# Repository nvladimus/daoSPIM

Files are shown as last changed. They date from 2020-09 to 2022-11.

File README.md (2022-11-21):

# daoSPIM




**D**ual-view **a**daptive **o**ptics **s**elected **p**lane **i**llumination **m**icroscope makes multiview light-sheet microscopy compatible with microfluidic devices, by correcting optical aberrations with a deformable mirror (DM). Its unique optical design allows correcting aberrations in two arms with a single DM simultaneously.
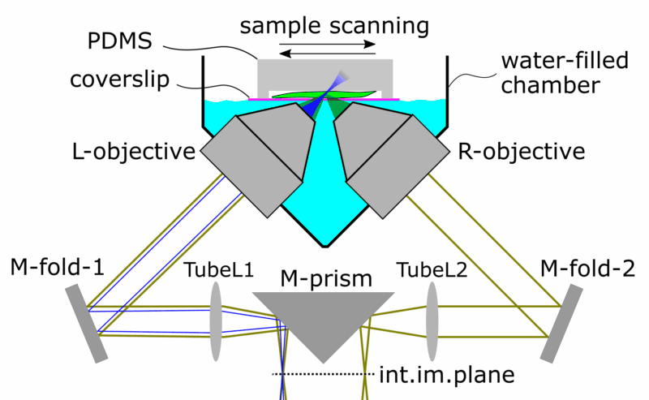
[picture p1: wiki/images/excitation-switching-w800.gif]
Optical layout: chamber


## Hardware overview
The [Wiki](https://github.com/nvladimus/daoSPIM/wiki/overview) page provides a high-level system overview. 

The [/wiki](./wiki) folder contains implementation details:
* [BOM](./wiki/BOM.xlsx)
* [CAD](./wiki/custom_parts_cad) files for custom-made mechanical parts
* [PCB](./wiki/arm_switcher) design files for arm switcher board

## Microscope control software
The microscope is controlled via [GUI program](./microscope_control) which links together:
- camera (Hamamatsu Orca Flash4.3)
- stage (ASI MS-2000)
- light-sheet generator (based on NI PCIe-6321 DAQ board and arm switcher)
- deformable mirror (ImagineOptics Mirao52e)
- electro-tunable lens (Optotune EL-16-40-TC-VIS-5D-C)

DM is optimized in a separate Jupyter [notebook](./dm_optimization/) using a fluorescent bead image. The resulting DM command can be loaded in the GUI  [program](./microscope_control) and used thereafter.

## Citation
If you use any code or materials from this repo in your work, please cite our work as

**Dual-view light-sheet imaging through tilted glass interface using a deformable mirror** \
Nikita Vladimirov, Friedrich Preusser, Jan Wisniewski, Ziv Yaniv, Ravi Anand Desai, Andrew Woehler, Stephan Preibisch. [Biomedical Optics Express, 2021](https://doi.org/10.1364/BOE.416737).

To cite the code specifically, please use the following DOI:



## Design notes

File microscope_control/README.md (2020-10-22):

## daoSPIM control
The software provides GUI for microscope control:
- advanced camera control (input and output triggers, acq. modes), 
- light sheet generation via galvo scanning (NI DAQmx task configuration)
- stage scanning (with TTL pulses at defined spatial intervals)
- deformable mirror control (loading and applying commands from file)
- electrotunable lens control (manual offsetting the ETL power)
- streaming images into HDF5 file (Fiji/BigDataViewer flavor) at high speed (currently up to 60Hz)




## Hardware requirements
 - PC with Windows 7/10, x64.
 - camera Hamamatsu Orca Flash4.3.
 - NI DAQmx PCIe board with at least 2 AO channels for galvo and laser modulation (e.g. PCIe-6321).
 - XY stage from ASI (MS-2000 controller).
 - ETL Optotune EL-16-40-TC-VIS-5D-C.
 - deformable mirror ImagineOptics Mirao52e.

### Installation 
(optional) Create and activate local environment from the command line, to keep things tidy
```
C:\Users\user\daoSPIM> cd microscope_control
C:\Users\user\daoSPIM> python -m venv venv
C:\Users\user\daoSPIM> venv\Scripts\activate.bat
(venv) C:\Users\user\daoSPIM>
```
Install dependencies 
```
pip install --upgrade pip
pip install -r requirements.txt
```
Launch the program
```
python dao_spim_control.py
```

### GUI overview
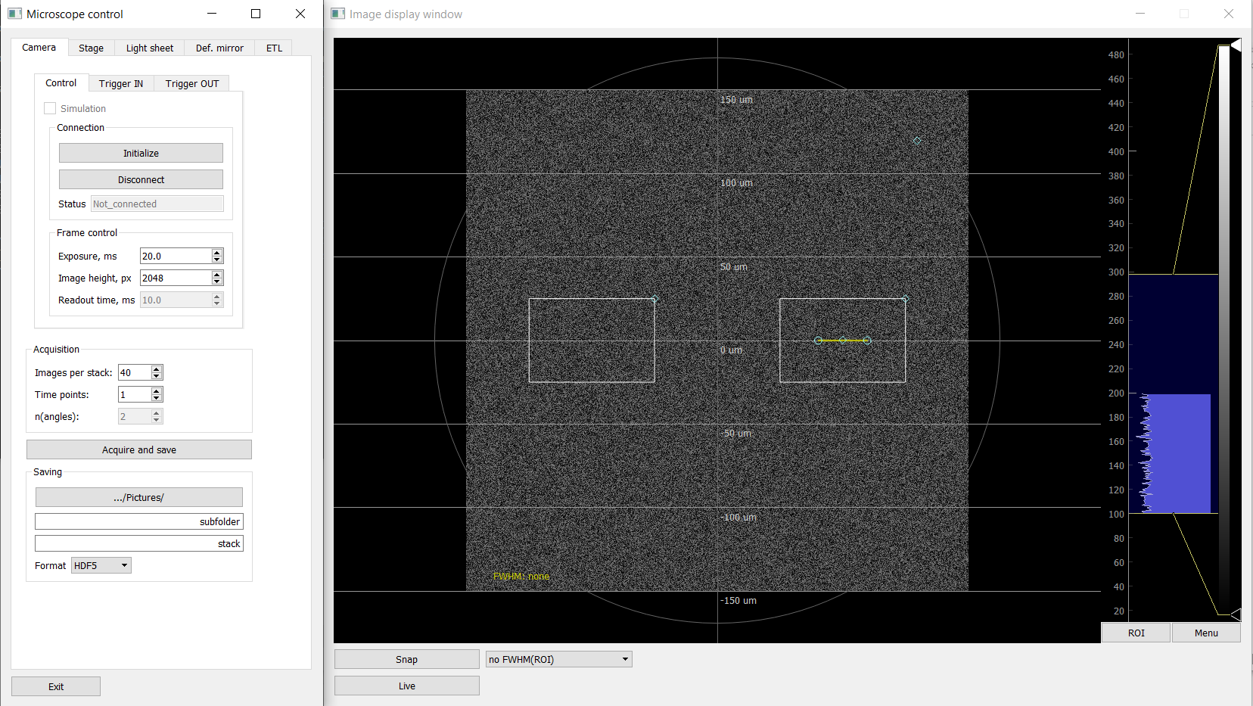
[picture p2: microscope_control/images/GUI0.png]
GUI


### Design principle
The code is still in development, but the author tried to keep it maximally modular and reusable. Each device is represented by a single file with GUI, controller and configuration code, independent from other devices. The main program file `dao_spim_control.py` connects these modules into a system. The GUI building is simplified by using a local library [widget.py](./src/widget.py) which takes care of PyQt5 low-level code.
See [device_template.py](./src/device_template.py) for example. 

The module files for these and other devices are independently available at [kekse](https://github.com/nvladimus/kekse) repo.

The camera control code was adapted from H.Babcock's [storm-control](https://github.com/ZhuangLab/storm-control/tree/master/storm_control/sc_hardware/hamamatsu) software.

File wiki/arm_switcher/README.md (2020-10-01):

# Arm switcher
This is a small Teensy-powered PCB that counts camera pulses and adds a user-defined voltage bias to the input signal after every *N* pulses. Designed to allow fast switching of light-sheet excitation laser (galvo) between left and right arms, to run in synch with camera. The software-based solution (eg in Python) would be too slow, hence this board.

PCB

## Inputs
* camera exposure pulses *Trig_in* (digital)
* galvo voltage *g_in* (analog) that makes a swipe motion for light sheet generation.

## Output
* analog signal *g_in + V0* (during first *N* camera pulses), *g_in + V1* (during next *N* pulses), then *g_in + V0* again, etc. 
* (for debugging) analog bias voltage alone: *V0* or *V1* .

## User-defined parameters:
   - camera pulse count *N* (>=1)
   - bias voltage *V0, V1* (-5 to +5 V)

## Setting parameters
Parameters are set via serial communication (baud rate 9600):
```
?ver #get the firmware version
n 10 #set switching period to 10 trigger pulses
?n #read the switching period
reset #reset the counter
v0 -0.45 #set voltage0 bias, [Volt]
v1 0.32 #set voltage1 bias, [Volt]
```

## Bill of materials
The PCB can be ordered from [Aisler](https://aisler.net/p/MTFTDGBD) (min. order 3 boards)

[Parts list](BOM.xlsx)

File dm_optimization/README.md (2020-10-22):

## Deformable mirror shape optimization 



### Software requirements
- Python 3.6, x64 (e.g. Anaconda)
- (optional) create and activate [local environment](/microscope_control#installation)
- Hamamatsu DCAM drivers
- Mirao52e dll drivers (x64)

### Hardware requirements
- PC with OS Windows 7/10
- camera Hamamatsu Orca4.3
- deformable mirror Mirao52e

### Sample requirements
- fluorescent bead resistant to bleaching,
- initial SNR is relatively high (ideally >10),
- only one fluorescent bead is present in the ROI, in both views,
- the bead is illuminated in wide-field or defocused light sheet mode. Using thin light sheet is discouraged to avoid light sheet walking off the bead (non-specific variation of the metric).

### Algorithm peculiarities
- the image metric is minimized;
- the gain grows in inverse proportion to the (decreasing) metric;
- the initial gain should be relatively small to avoid divergence (hopping on big bumps of the gradient);
- the algorithm tracks the position of a bead within the ROI and adjusts the ROI position if the bead drifts over time;
- the shape of DM is averaged between left and right halfs of the aperture, to add stability.

### Disclaimer
This notebook execution depends on particular hardware configuration and experimental conditions, and cannot be exactly reproduced. It was run several times after the original experiment in simulation mode to make the presentation more clear, so the cells are not numbered consecutively.

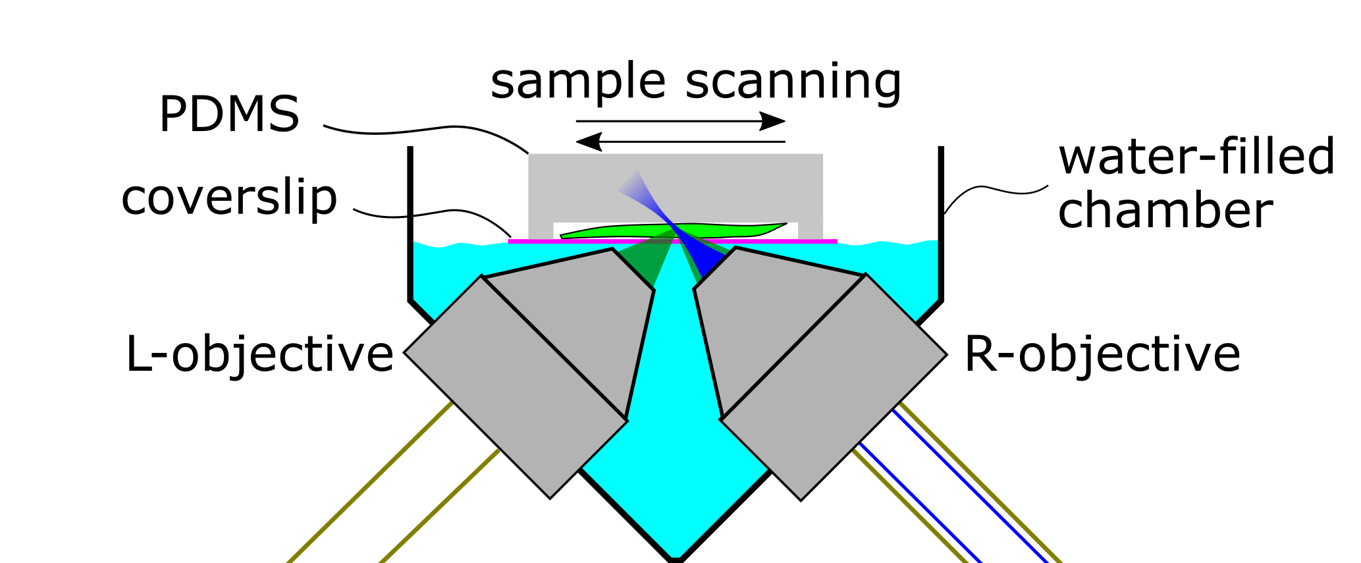
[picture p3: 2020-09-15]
wiki/images/ChamberOpticalLayout.png

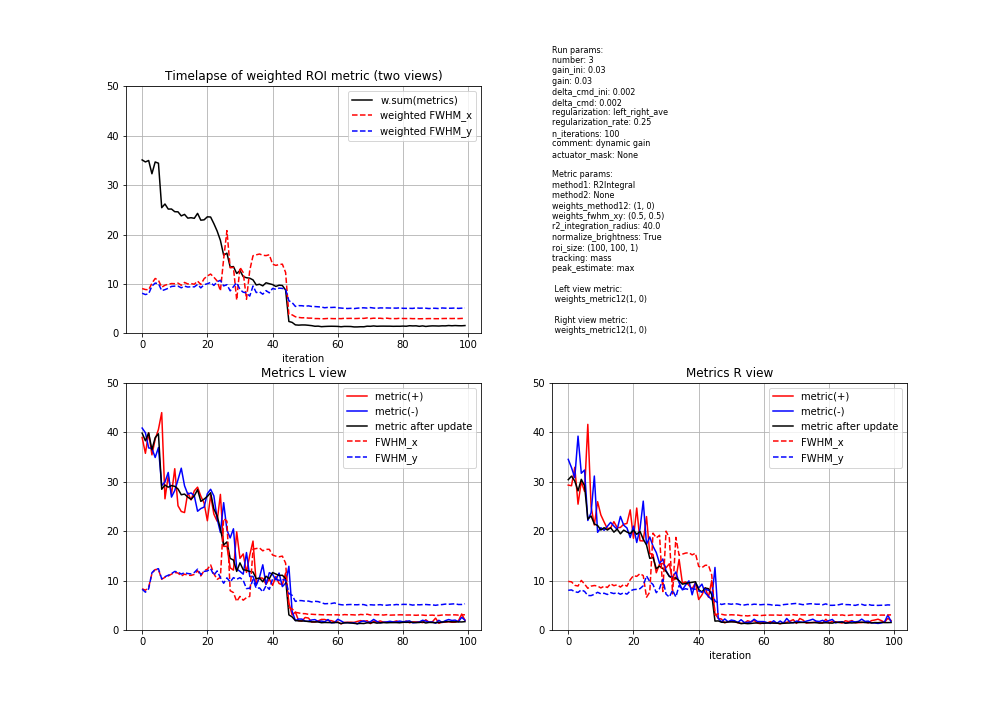
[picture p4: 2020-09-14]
dm_optimization/2020-02-18_optimization_examples/Run3_report.png

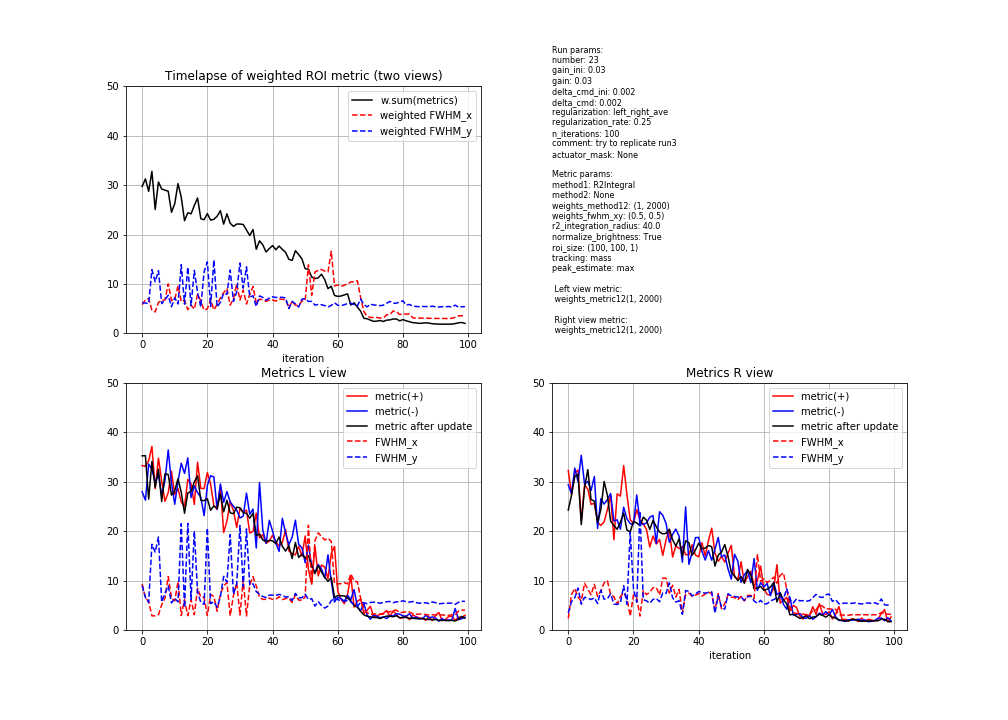
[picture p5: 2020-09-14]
dm_optimization/2020-02-18_optimization_examples/Run23_report.png

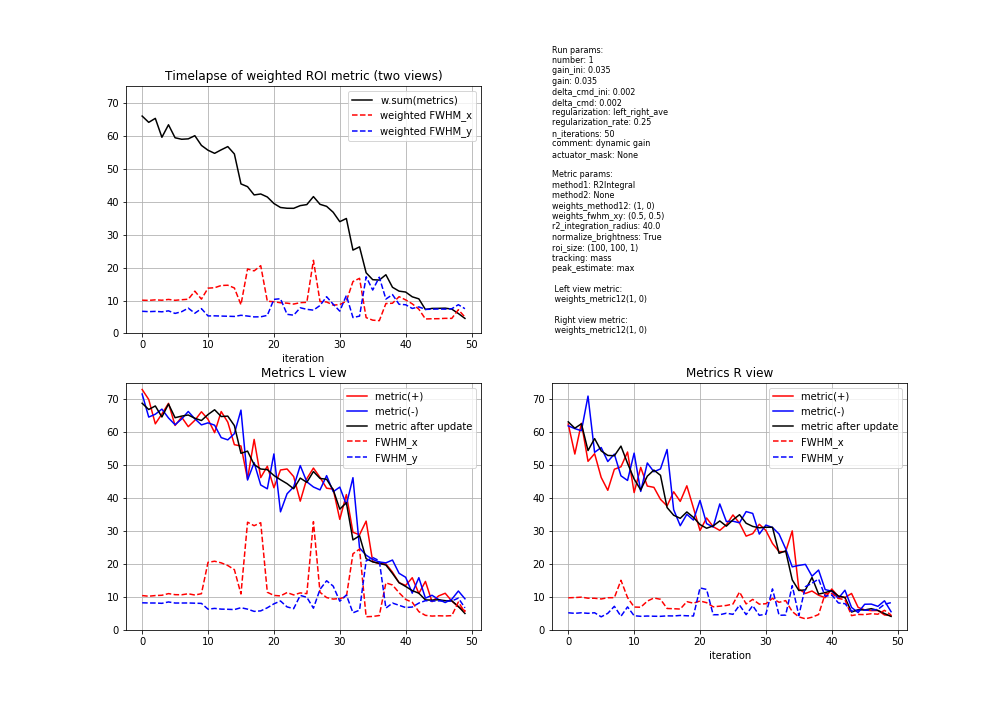
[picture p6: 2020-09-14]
dm_optimization/2020-02-18_optimization_examples/Run1_report.png

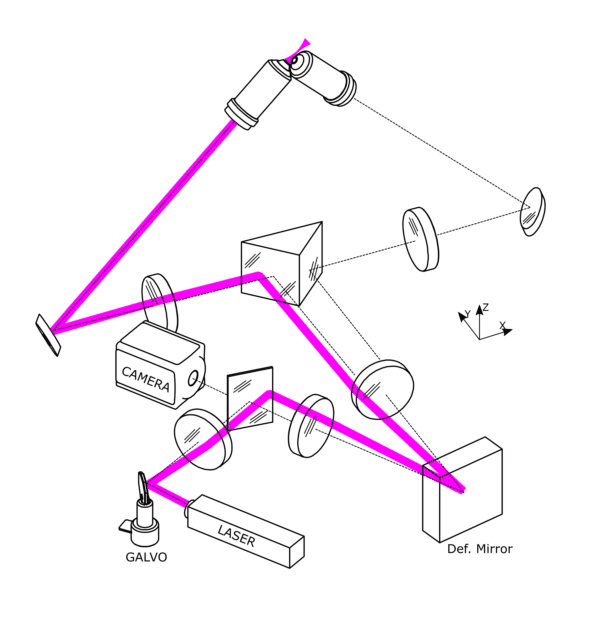
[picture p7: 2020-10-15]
wiki/images/excitation_switching3d_w600.gif

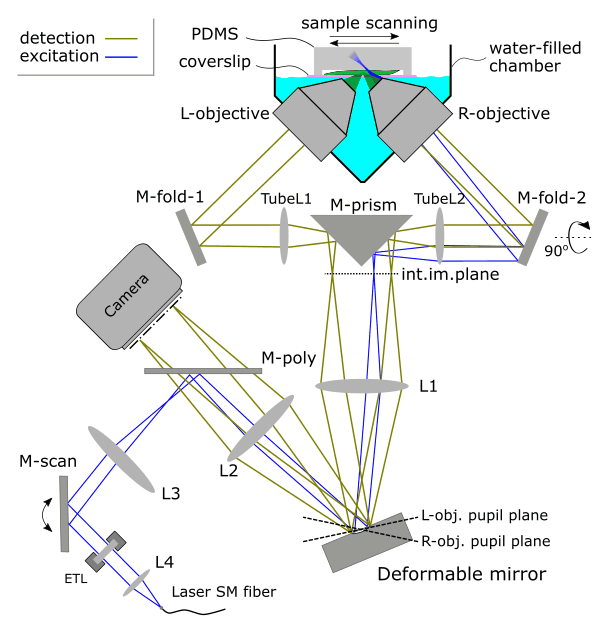
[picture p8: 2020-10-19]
wiki/images/excitation-switching.gif

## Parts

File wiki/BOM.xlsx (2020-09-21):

Component | Product | Manufacturer/Distributor | Price, EUR | Qty | Subtotal
Optomechanics
Objective | 40x/0.8 water-dipping apochromatic objective WD 3.5 mm, N40X-NIR. | Nikon / Thorlabs | 2850 | 2 | 5700
Objective mount | Z-Axis Translation Mount, 30 mm Cage Compatible, SM1Z. | Thorlabs | 187 | 2 | 374
Tube lens (TubeL1, TubeL2) | f=250mm mounted achromats, 25mm diam., AC254-250-A-ML | Thorlabs | 96 | 2 | 192
Prism mirror (M-prism) | Enhanced aluminium right angle mirror, legs 50 mm, #47-006 | Edmund Optics | 310 | 1 | 310
Prism mirror mount | Angle adjustment stage: Mini rotation stage 7R7E | Standa | 232 | 1 | 232
 | Connecting plate: 2CP7R7-273 | Standa | 90 | 1 | 90
 | XY adjustment: Low Profile Two-Axis Aluminium Translation Stage 7T273-10T | Standa | 384 | 1 | 384
Folding mirror (M-fold1, M-fold2) | Broadband Dielectric Elliptical Mirror, BBE1-E02 | Thorlabs | 92 | 2 | 184
Folding mirror mount | 45° Mount for 1" Elliptical Optics, H45E1 | Thorlabs | 114 | 2 | 228
 | Kinematic mount, KM100 | Thorlabs | 36 | 2 | 72
Relay lens L2 | f=400mm achromat, AC508-400-A-ML, 50.8 mm diam. | Thorlabs | 135 | 1 | 135
Relay lens L1 | f=450 mm achromat, diam. 40 mm, # 49-282 | Edmund Optics | 141 | 1 | 141
Deformable mirror, DM | Mirao52e | Imagine Optics | 21670 | 1 | 21670
Camera | Orca Flash 4v3 | Hamamatsu | 12500 | 1 | 12500
Detection cleanup filter | Quad-band filter ZET405/488/561/640mv2, 25.4mm Diam., mounted. | Chroma | 476 | 1 | 476
Laser | Skyra fiber-coupled, 405, 488, 561, 638 nm. MF-561-638-488-405-050-050-050-050-130 | Cobolt | 21765 | 1 | 21765
Fiber collimator assembly | Lens L4: f=10 mm mounted achromat, AC080-010-A-ML | Thorlabs | 67 | 1 | 67
 | Thread adapter: S1TM12 | Thorlabs | 22 | 1 | 22
 | Fiber coupler: FC/APC fiber adapter, SM1FCA | Thorlabs | 30 | 1 | 30
Electro-tunable lens assembly, ETL | ETL: EL-16-40-TC-VIS-5D-C, -3 to +2 diopter, 16 mm aperture. | Optotune | 780 | 1 | 780
 | Lens Driver 4i | Optotune | 280 | 1 | 280
 | Hirose 6-way cable | Optotune | 85 | 1 | 85
 | XY adjustment: XY translation stage, ST1XY-S/M. | Thorlabs | 364 | 1 | 364
 | Folding mirror: 1" Broadband Dielectric Elliptical Mirror, BBE1-E02. | Thorlabs | 92 | 1 | 92
 | Mirror mount: kinematic mirror mount KCB1EC/M | Thorlabs | 189 | 1 | 189
Scanning mirror, M-scan | Galvo mirror: 1D galvo system GVS001, silver-coated | Thorlabs | 937 | 1 | 937
 | Adapter: 30 mm Cage System Adapter GCM001 | Thorlabs | 135 | 1 | 135
Scan lens L3 | Mounted achromat f=125 mm, AC254-125-A-ML | Thorlabs | 96 | 1 | 96
Polychroic mirror, M-poly | ZT405/488/561/640rpcv2-UF2, 26 x 38 x 2mm, ID IN061199 | Chroma | 495 | 1 | 495
XY scanning motorized stage | Stage: 120x75mm travel, FTP flat-top stage with TE2000 bottom plate, 4TPI, scan-optimized X axis, without anti-backlash gear. Model MS-2000. #S562-2235B | ASI | 6950 | 1 | 6950
 | Controller: MS2000, with TTL pulse (ENC_INT) firmware. | ASI | 3600 | 1 | 3600
 | Stage Insert | custom-made | 0 | 1 | 0
Z-translation manual stage | ULTRAlign™ Precision stage, 12.7 mm travel, M-461-X-M | Newport | 526 | 1 | 526
 | Micrometer head, high-resolution, HR-13. | Newport | 128 | 1 | 128
Sample holder for 22x22 mm coverslip | Custom design, machined from stainless steel | Protolabs | 450 | 1 | 450
Optical table | T46H | Nexus/Thorlabs | 6301 | 1 | 6301
Computer hardware
Acquisition workstation | Precision Tower 7910, Windows 10 Professional | Dell | 6630 | 1 | 6630
DAQ | NI PCIe-6321 Multifunction I/O Device | National Instruments | 750 | 1 | 750
 | Connector block BNC 2110 | National Instruments | 450 | 1 | 450
 | BNC shielded cable SHC68-68-EPM | National Instruments | 167 | 1 | 167
Software
Microscope control | Custom-written, Python 3.6, PyQt5 | self | 0 | 1 | 0
Optical simulations | Zemax Optics Studio | Zemax | 4151 | 1 | 4151
CAD design | Autodesk Inventor, Education license | Autodesk | 0 | 1 | 0
 |  |  |  | Total | 98128

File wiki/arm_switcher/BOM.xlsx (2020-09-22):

Component | Model | Price, EUR | Qty | Subtotal
Arduino-compatible MCU | Teensy 2.0 | 28 | 1 | 28
DAC breakout board | MCP4725 | 3.5 | 1 | 3.5
opAmp | UA741 | 0.4 | 2 | 0.8
Voltage inverter | ICL7660 | 1.9 | 1 | 1.9
Power regulator 5V | L7805A | 0.46 | 1 | 0.46
BNC sockets | see detailed_bom.csv | 1 | 4 | 4
Barrel connector | see detailed_bom.csv | 0.5 | 1 | 0.5
Resistors, capacitors, trimpots | see detailed_bom.csv | 2 | 1 | 4
custom PCB | https://aisler.net/p/MTFTDGBD | 12 | 1 | 12
 |  |  | Total | 55.16

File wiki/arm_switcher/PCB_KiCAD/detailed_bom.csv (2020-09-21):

Reference | Value | Footprint | Datasheet | Category | DK_Datasheet_Link | DK_Detail_Page | Description | Digi-Key_PN | Family | MPN | Manufacturer | Status | Height | Manufacturer_Name | Manufacturer_Part_Number | Mouser Part Number | Mouser Price/Stock
U1 | Teensy2.0_(Arduino) | teensy_footprints:Teensy2.0
R1 | 10k | Resistor_THT:R_Axial_DIN0207_L6.3mm_D2.5mm_P10.16mm_Horizontal | ~
J1 | Trigger IN | my_components:BNC_female_jack_TE_1-1634505-0 | ~
J2 | Galvo signal IN | my_components:BNC_female_jack_TE_1-1634505-0 | ~
J3 | DC bias out | my_components:BNC_female_jack_TE_1-1634505-0 | ~
U2 | MCP4725_bkt | my_components:MCP4725
U3 | L7805CV | digikey-footprints:TO-220-3 | http://www.st.com/content/ccc/resource/technical/document/datasheet/41/4f/b3/b0/12/d4/47/88/CD00000444.pdf/files/CD00000444.pdf/jcr:content/translations/en.CD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 | Integrated Circuits (ICs) | http://www.st.com/content/ccc/resource/technical/document/datasheet/41/4f/b3/b0/12/d4/47/88/CD00000444.pdf/files/CD00000444.pdf/jcr:content/translations/en.CD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 | /product-detail/en/stmicroelectronics/L7805CV/497-1443-5-ND/585964 | IC REG LINEAR 5V 1.5A TO220AB | 497-1443-5-ND | PMIC - Voltage Regulators - Linear | L7805CV | STMicroelectronics | Active
C1 | 0.33uF | Capacitor_THT:CP_Radial_Tantal_D4.5mm_P2.50mm | ~
U4 | ICL7660 | Package_DIP:DIP-8_W7.62mm | http://datasheets.maximintegrated.com/en/ds/ICL7660-MAX1044.pdf
C2 | 10uF | Capacitor_THT:CP_Radial_D4.0mm_P1.50mm | ~
C3 | 10uF | Capacitor_THT:CP_Radial_D4.0mm_P1.50mm | ~
IC1 | UA741CP | digikey-footprints:DIP-8_W7.62mm | http://www.ti.com/lit/ds/symlink/ua741.pdf |  |  |  | Single op-amp,UA741CP 1MHz DIP8, tube Texas Instruments UA741CP Op Amp, 1MHz, 8-Pin PDIP |  |  |  |  |  | 5.08 | Texas Instruments | UA741CP | 595-UA741CP | https://www.mouser.com/Search/Refine.aspx?Keyword=595-UA741CP
R3 | 1k | Resistor_THT:R_Axial_DIN0207_L6.3mm_D2.5mm_P10.16mm_Horizontal | ~
R4 | 1k | Resistor_THT:R_Axial_DIN0207_L6.3mm_D2.5mm_P10.16mm_Horizontal | ~
IC2 | UA741CP | digikey-footprints:DIP-8_W7.62mm | http://www.ti.com/lit/ds/symlink/ua741.pdf |  |  |  | Single op-amp,UA741CP 1MHz DIP8, tube Texas Instruments UA741CP Op Amp, 1MHz, 8-Pin PDIP |  |  |  |  |  | 5.08 | Texas Instruments | UA741CP | 595-UA741CP | https://www.mouser.com/Search/Refine.aspx?Keyword=595-UA741CP
J4 | (galvo + DC bias) OUT | my_components:BNC_female_jack_TE_1-1634505-0 | ~
R6 | 1k | Resistor_THT:R_Axial_DIN0207_L6.3mm_D2.5mm_P10.16mm_Horizontal | ~
R5 | 1k | Resistor_THT:R_Axial_DIN0207_L6.3mm_D2.5mm_P10.16mm_Horizontal | ~
R2 | 10k | Resistor_THT:R_Axial_DIN0207_L6.3mm_D2.5mm_P10.16mm_Horizontal | ~
RV1 | 10k | digikey-footprints:PinHeader_1x3_P2.5mm_Drill1.1mm | ~
RV2 | 10k | digikey-footprints:PinHeader_1x3_P2.5mm_Drill1.1mm | ~
J5 | PJ-202A | digikey-footprints:Barrel_Jack_5.5mmODx2.1mmID_PJ-202A | https://www.cui.com/product/resource/digikeypdf/pj-202a.pdf | Connectors, Interconnects | https://www.cui.com/product/resource/digikeypdf/pj-202a.pdf | /product-detail/en/cui-inc/PJ-202A/CP-202A-ND/252007 | CONN PWR JACK 2X5.5MM KINKED PIN | CP-202A-ND | Barrel - Power Connectors | PJ-202A | CUI Inc. | Active

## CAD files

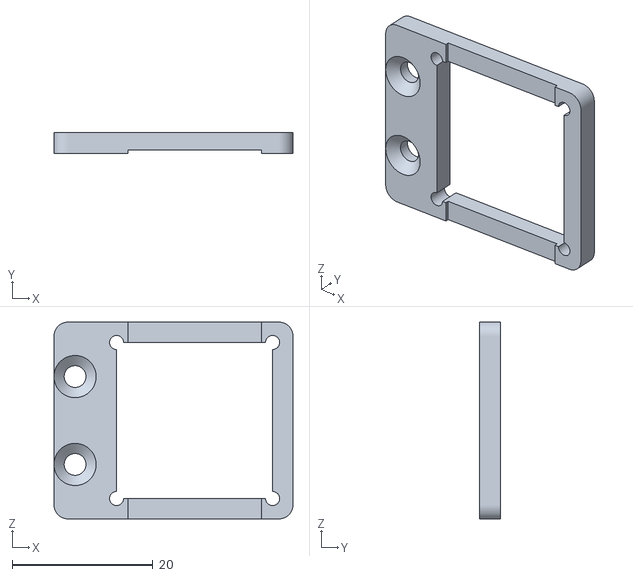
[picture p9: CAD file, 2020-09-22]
wiki/custom_parts_cad/Sample_holder_cslip22x22mm_part1.stl
34.0 x 3.00 x 28.0

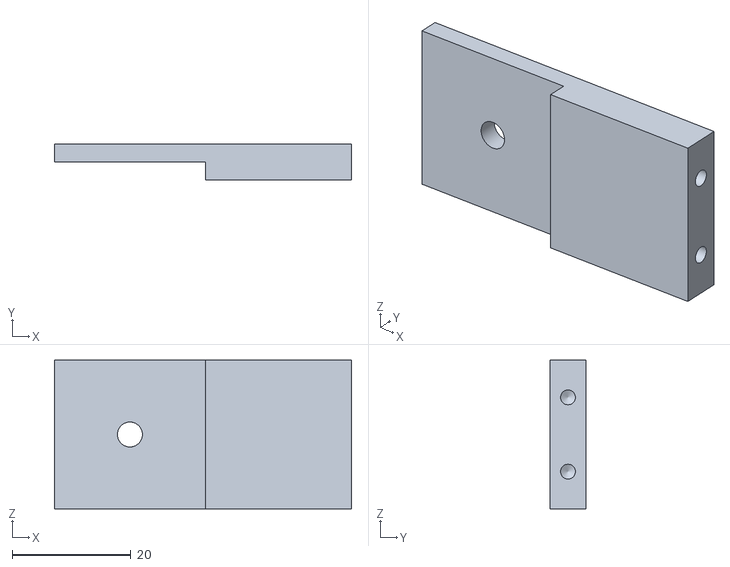
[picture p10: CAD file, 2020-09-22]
wiki/custom_parts_cad/Sample_holder_cslip22x22mm_part2.stl
50.0 x 6.00 x 25.0

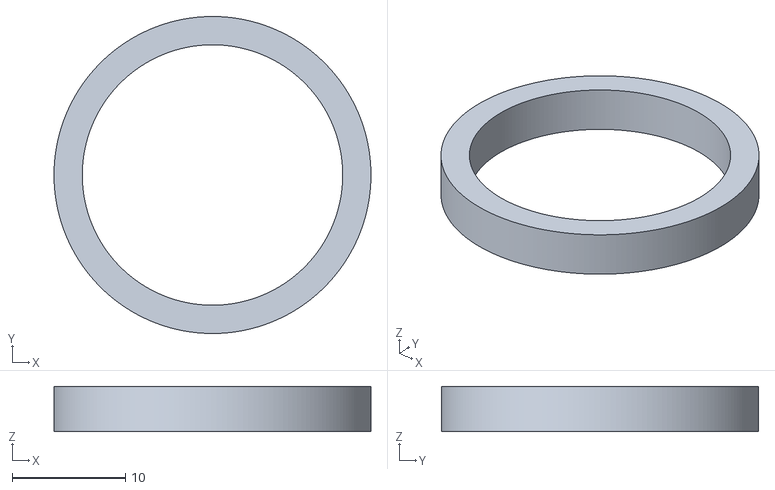
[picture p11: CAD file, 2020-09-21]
wiki/custom_parts_cad/O-Ring-OD28-ID23-H3mm.stl
28.0 x 28.0 x 4.00

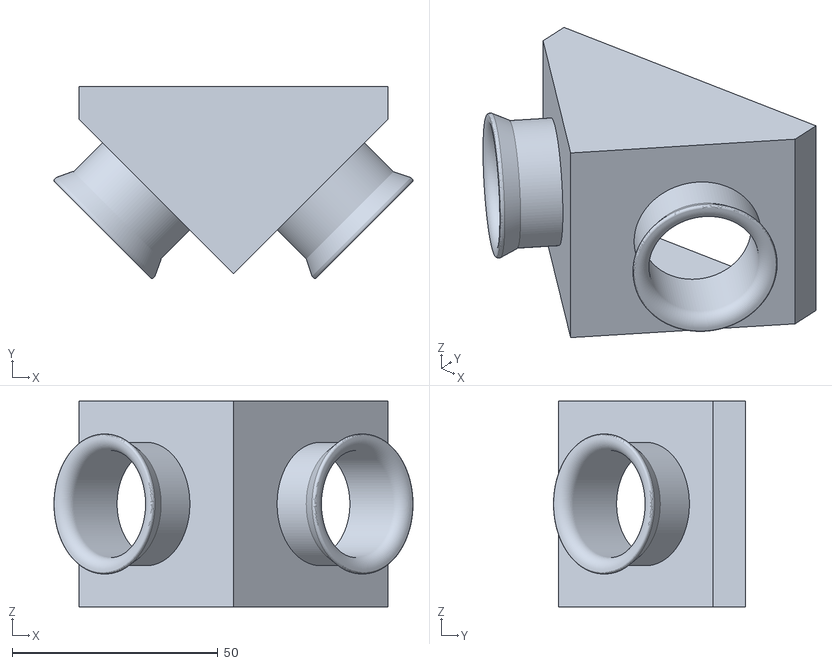
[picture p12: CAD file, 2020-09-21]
wiki/custom_parts_cad/Chamber.stl
87.3 x 46.7 x 50.0

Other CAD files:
wiki/custom_parts_cad/Chamber.ipt
wiki/custom_parts_cad/O-Ring-OD28-ID23-H3mm.ipt
wiki/custom_parts_cad/Sample_holder_cslip22x22mm_part1.ipt
wiki/custom_parts_cad/Sample_holder_cslip22x22mm_part2.ipt

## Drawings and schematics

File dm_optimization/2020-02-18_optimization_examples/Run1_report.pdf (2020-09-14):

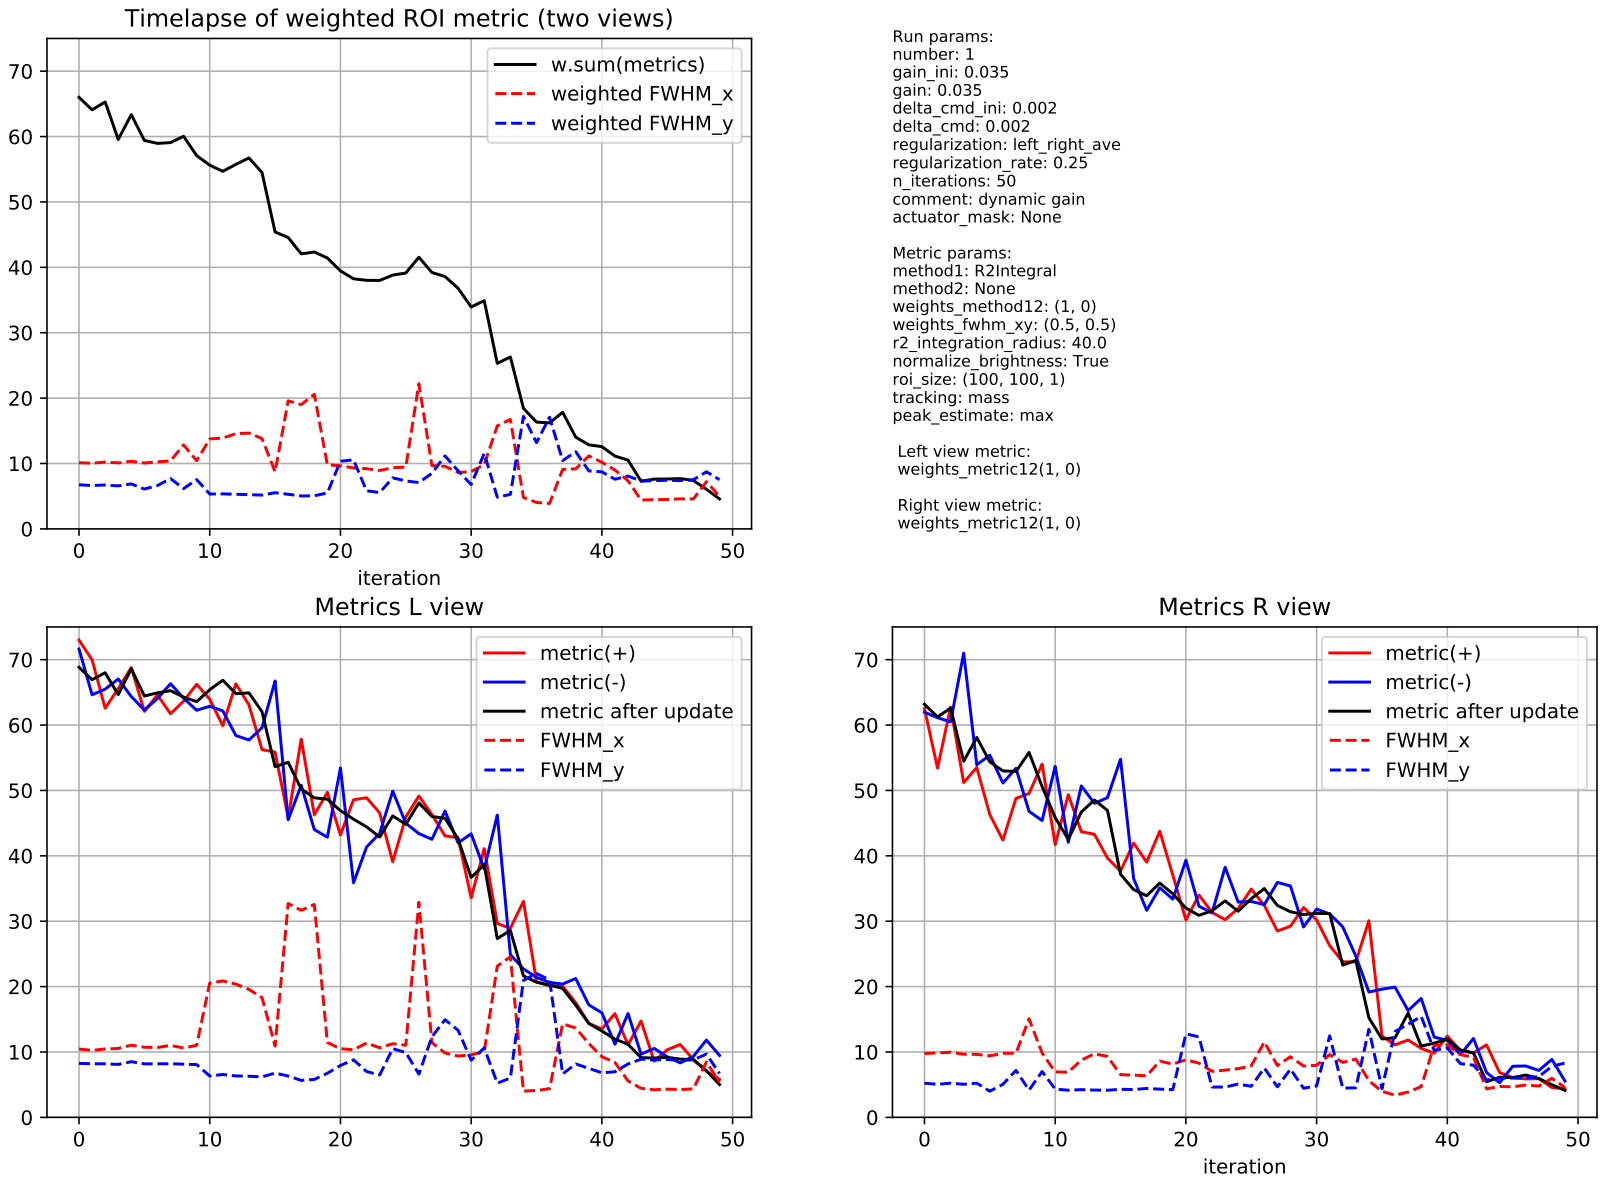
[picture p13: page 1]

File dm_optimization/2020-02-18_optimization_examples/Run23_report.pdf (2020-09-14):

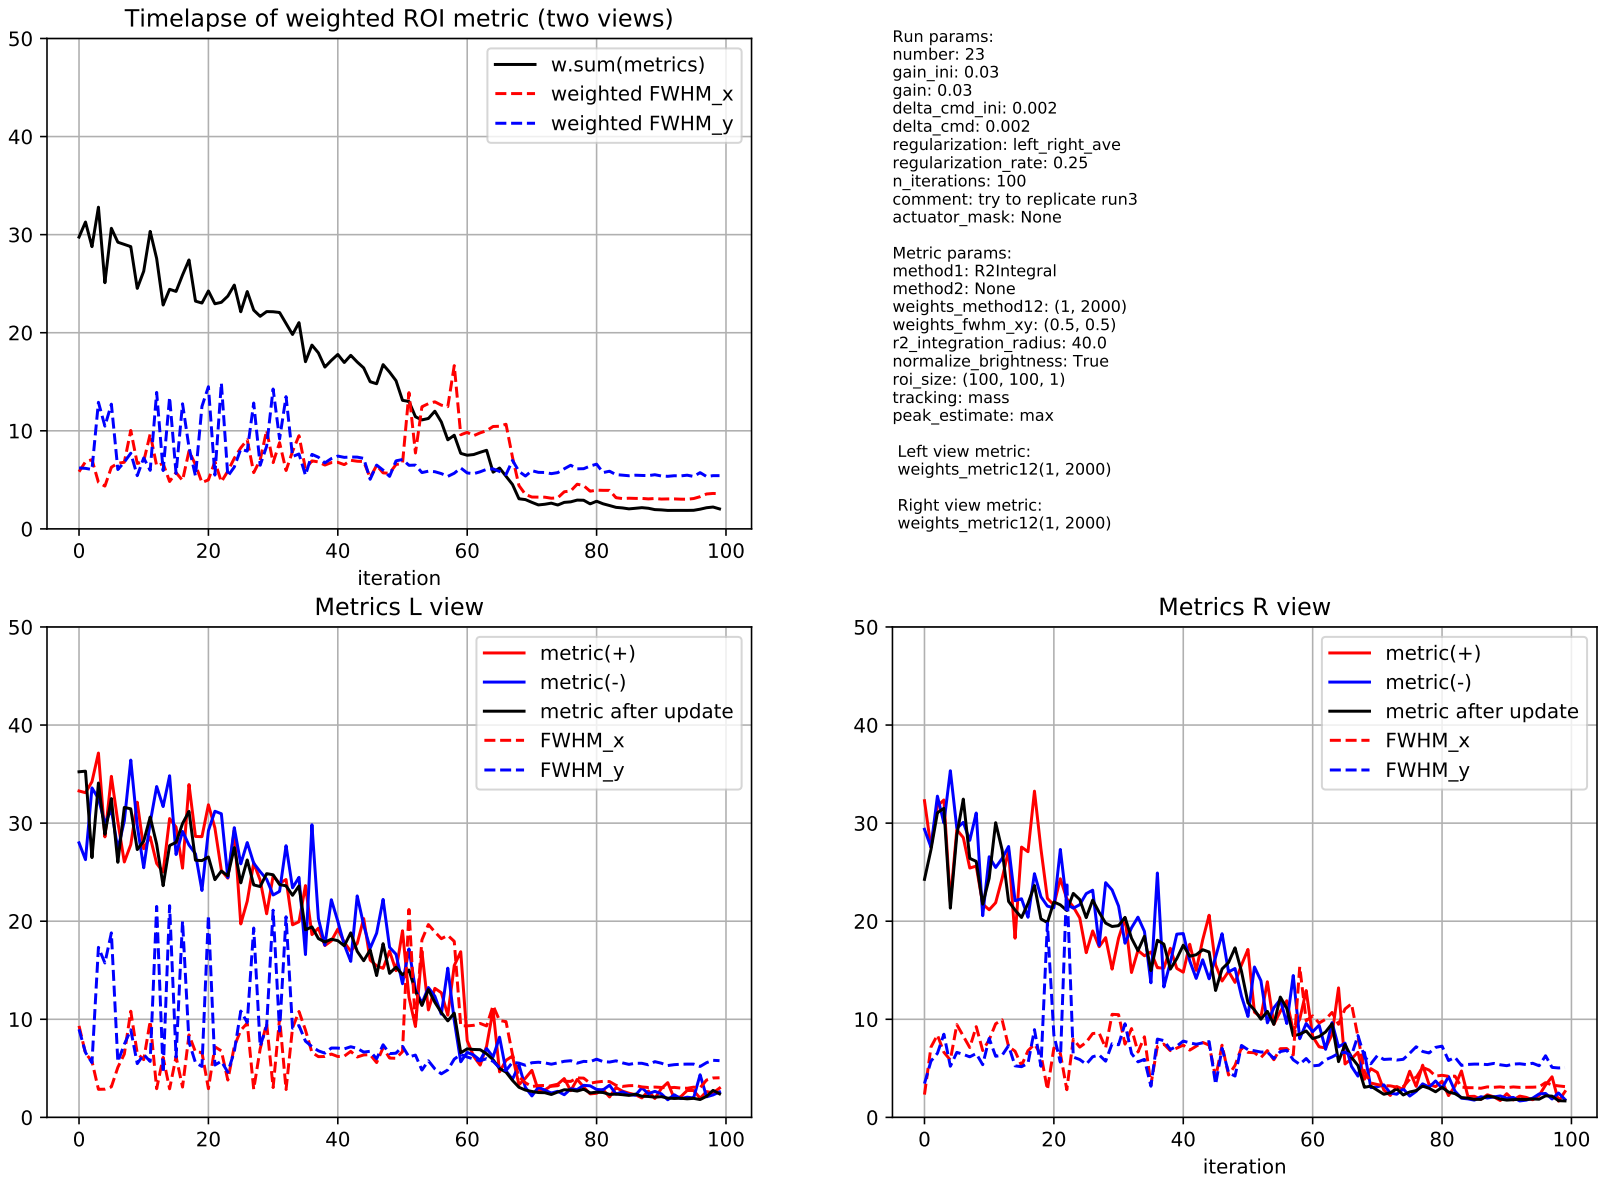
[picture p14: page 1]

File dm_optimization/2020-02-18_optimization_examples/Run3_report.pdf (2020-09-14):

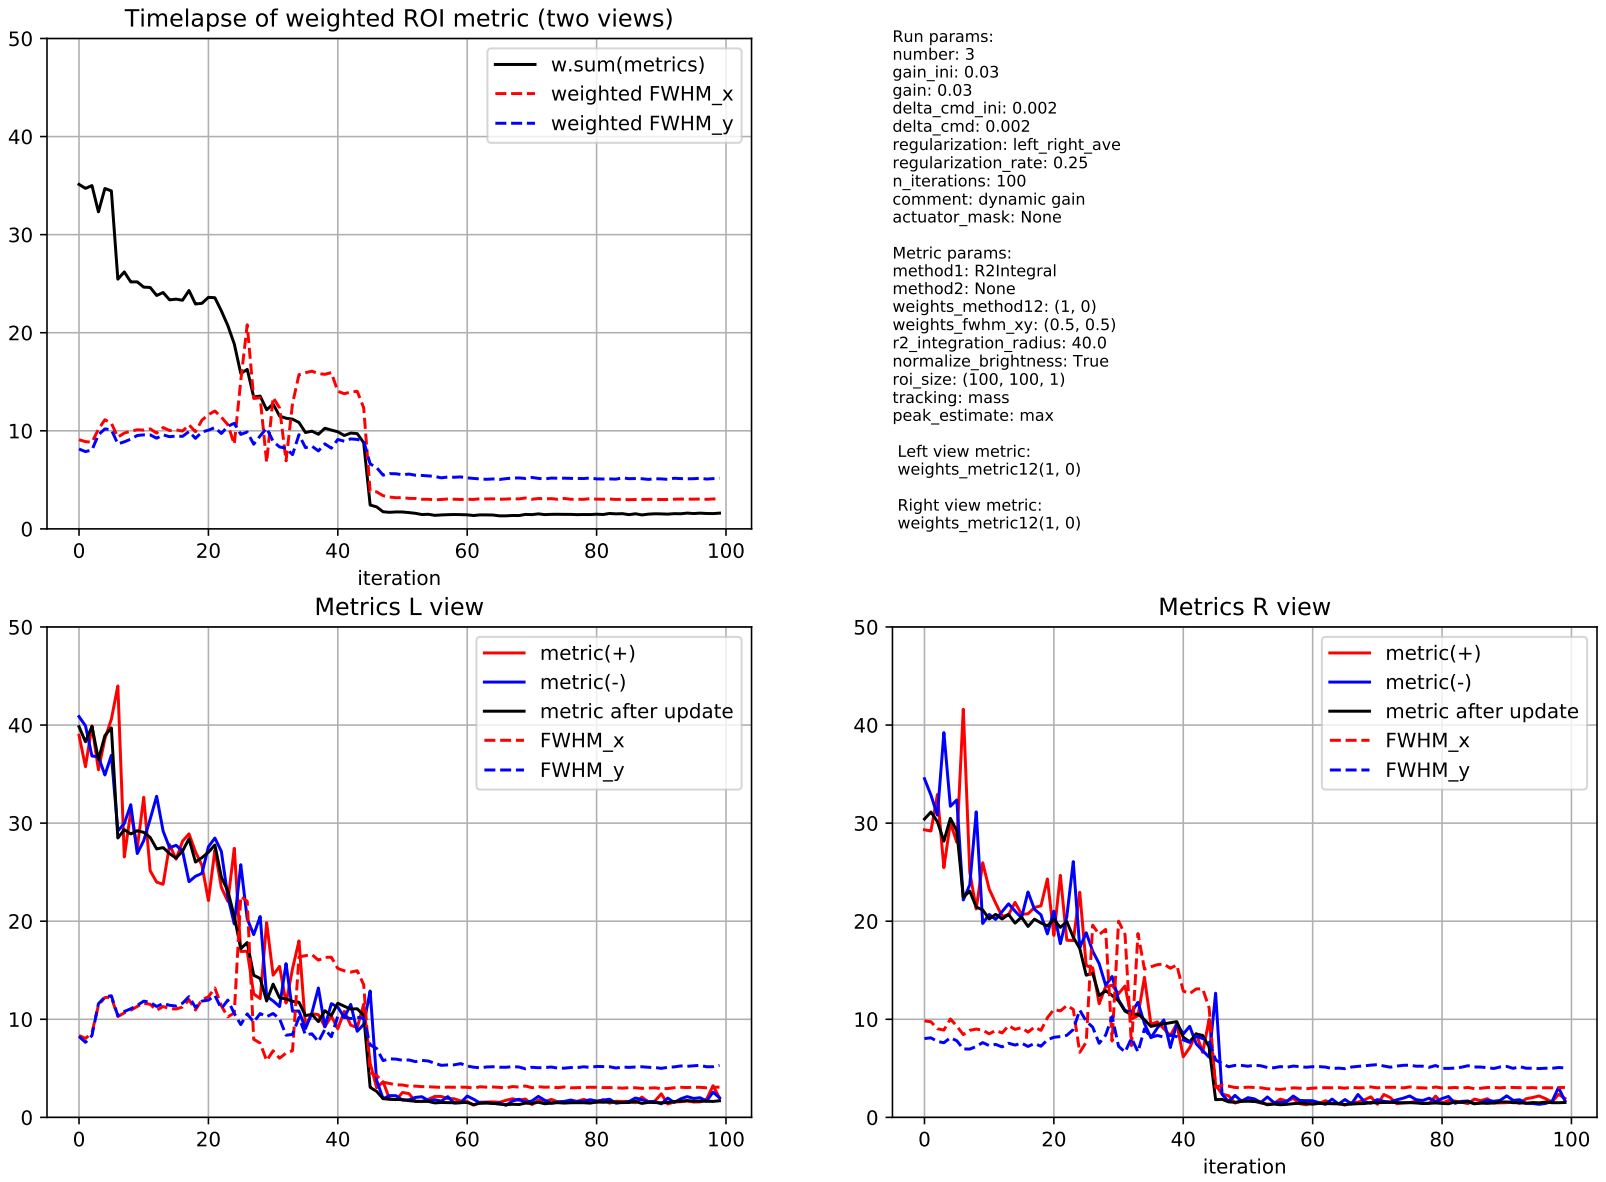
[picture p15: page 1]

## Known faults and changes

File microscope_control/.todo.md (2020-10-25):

## Burning
- [ ] Replace time.sleep() with a QTimer method to stop blocking threads
- [ ] make sure methods are thread-safe: image acquisition, image writing, live imaging
- [ ] add XY scanning and tiling
- [ ] add low-mag WF microscope on top

## Long-term
- [ ] separate GUI from core, use Qt Creator for new UI files
- [ ] make project structure more logical:
    - /devices
    - /gui
    - /utils (eg. image writer, gaussian fitters, optimizer)
    - /tests

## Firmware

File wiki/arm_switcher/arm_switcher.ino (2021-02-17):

// This code counts rising edges of an input trigger (from camera or stage) and 
// switches analog output voltage setting after every N trigger pulses.
// In this version, analog output is bipolar (-5..5V), by using DAC chip MCP4725, voltage inverter ICL7660S and opAmp UA741. 
// see /wiring_fritzing folder for detals.
// tested on Teensy 2.0, should work on Arduino, too.
// Default speed of Arduino Wire library is 100KHz. The Adafruit MCP4725 library can run at speed 400KHz by setting the TWBR = 12;
// Nikita Vladimirov, 2019.
#include <Wire.h>
#include <Adafruit_MCP4725.h>

const float VCC = 5.0; // power supply voltage. Don't use USB power, it's noisy and can be < 5V.
const float opAmp_gain = 2.0; // multiplication factor of the opAmp, equal to 1 + R1/R2, where R1, R2 are resistor values.
const byte interruptPin = 7; // Teensy 2.0, interrupt pins are: 5, 6, 7, 8. This digital pin must be capable of Interrupt mode.
const byte ledPin = 11; // blink every time a pulse is detected
const char _version[16] = "2021.01";

volatile int counter;
volatile int counter_old;
volatile byte ledState;
Adafruit_MCP4725 dac; // constructor
float voltage_out_0 = -0.42;
float voltage_out_1 = 0.35;
int swipe_ms = 2; // galvo swipe duration, used to delay switching (switching AFTER galvo swipe is complete)
int debounce_delay_ms = 1; // minimum input trigger duration, for digital debouncing
int n_pulses_switch_period = 10; // DAC output will alternate between voltage_out_0 and voltage_out_1 with this period
uint16_t dac_value; 
uint16_t dac_value_0; 
uint16_t dac_value_1; 
  
void setup() {
  Serial.begin(9600);
  pinMode(ledPin, OUTPUT);
  digitalWrite(ledPin, HIGH);
  ledState = LOW;
  
  pinMode(interruptPin, INPUT_PULLUP);
  attachInterrupt(digitalPinToInterrupt(interruptPin), count, RISING);
  counter = 0;
  counter_old = 0;
  
  dac.begin(0x62); // if unsure, use I2C scanner to find the I2C address of your MCP4725: http://henrysbench.capnfatz.com/henrys-bench/arduino-projects-tips-and-more/arduino-quick-tip-find-your-i2c-address/
  dac_value_0 = volts2dac_value(voltage_out_0);
  dac_value_1 = volts2dac_value(voltage_out_1);
  dac_value = dac_value_0;
}

void loop() {
  if(counter > counter_old){
    Serial.println(counter);
    counter_old = counter;
    digitalWrite(ledPin, ledState);
    if(counter_old % n_pulses_switch_period == 0){
      delay(swipe_ms);
      if(dac_value == dac_value_0) dac_value = dac_value_1;
      else dac_value = dac_value_0;
    }
  }
  dac.setVoltage(dac_value, false); // this command should always run as fast as possible, since it doesn't hold the value.
  readCommand();
}

void count() {
  delay(debounce_delay_ms); // filter out fluke sub-ms pulses
  if (digitalRead(interruptPin) == HIGH) {
    counter++;
    ledState = !ledState;
  }
}

uint16_t volts2dac_value(float volts_out){
  // return(int(volts_out / VCC * 4095.0)); //unipolar case, no amplifier
  float v_dac;
  v_dac = (volts_out + VCC) / opAmp_gain;
  return(int(v_dac / VCC * 4095.0));
}

void readCommand() {
    boolean newCommandReceived = false;
    char receivedChars[16];
    char rc;
    byte ic = 0;
    while (Serial.available() > 0  && newCommandReceived == false)
    {
      rc = Serial.read();
      receivedChars[ic] = rc;
      ic++;
      delay(2);  //slow looping to allow buffer to fill with next character
      if(rc == '\n' || rc == '\r'){
        newCommandReceived = true;
        receivedChars[ic] = '\0';
      }
    }
    if(newCommandReceived){
      parseCommand(receivedChars);
    }
}

void parseCommand(char receivedChars[]){
  char *keywordString;
  char *token;
  
  keywordString = strstr(receivedChars, "n ");
  if (keywordString != NULL){ // set the switching period
    token = strtok(keywordString," "); //chop the keyword
    token = strtok(NULL, "\n"); //get the number
    n_pulses_switch_period = atoi(token);
    Serial.println(n_pulses_switch_period);
  }
  
  keywordString = strstr(receivedChars, "?n");
  if (keywordString != NULL){
    Serial.println(n_pulses_switch_period);
  }

  keywordString = strstr(receivedChars, "?ver");
  if (keywordString != NULL){
    Serial.println(_version);
  }
  
  keywordString = strstr(receivedChars, "reset");
  if (keywordString != NULL){
    counter = 0;
    counter_old = 0;
    dac_value = dac_value_0;
    Serial.println(counter);
  }
  
  keywordString = strstr(receivedChars, "v0 ");
  if (keywordString != NULL){
    token = strtok(keywordString," "); //chop the keyword
    token = strtok(NULL, "\n"); //get the number
    voltage_out_0 = atof(token);
    dac_value_0 = volts2dac_value(voltage_out_0);
    Serial.println(voltage_out_0);
  }

  keywordString = strstr(receivedChars, "v1 ");
  if (keywordString != NULL){
    token = strtok(keywordString," "); //chop the keyword
    token = strtok(NULL, "\n"); //get the number
    voltage_out_1 = atof(token);
    dac_value_1 = volts2dac_value(voltage_out_1);
    Serial.println(voltage_out_1);
  }
}

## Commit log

2020-03-28 first draft of camera module
2020-03-29 replaced stage (frontend only), need more work.
2020-05-07 camera module debugged on hardware
2020-05-07 ETL and DM work, stage control needs attention
2020-05-11 debugging ASI stage control
2020-05-14 debugged stage and camera triggers. Next: bead test.
2020-05-19 addressed stage backlash
2020-05-20 brought back scanning thread
2020-07-02 no signals pass between threads, bummer
2020-07-02 fixed thread signals bug, hardware test pass
2020-09-21 chamber and o-ring CAD files
    [Chamber.ipt, Chamber.stl, O-Ring-OD28-ID23-H3mm.ipt, O-Ring-OD28-ID23-H3mm.stl]
2020-09-21 folder rename
    [Chamber.ipt, Chamber.stl, O-Ring-OD28-ID23-H3mm.ipt, O-Ring-OD28-ID23-H3mm.stl]
2020-09-21 arm switcher upload
    [BOM.xlsx, detailed_bom.csv]
2020-09-22 updated libraries to fix broken links
    [BOM.xlsx]
2020-09-22 sample holder parts
    [Sample_holder_cslip22x22mm_part1.ipt, Sample_holder_cslip22x22mm_part1.stl, Sample_holder_cslip22x22mm_part2.ipt, Sample_holder_cslip22x22mm_part2.stl]
2020-12-14 moved most stage widgets to their ui file
2020-12-14 moving stage gui to .ui file is finished

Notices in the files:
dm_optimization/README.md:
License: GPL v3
